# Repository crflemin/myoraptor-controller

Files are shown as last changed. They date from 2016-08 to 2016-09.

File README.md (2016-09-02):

# myoraptor-controller
This is the second iteration (but let's call it version 1.0) of a project combining the Raptor Reloaded 3D printed prosthetic with a MyoWare EMG sensor, a DC motor, and a Teensy 3.2. The goal is to build a prosthetic hand that responds to muscle contractions. I worked on the first iteration with an exceptional high school student who prototyped the design of the electronics control system using an Arduino Uno, breadboard, and wires. Shashi Jain designed the linear rail adapter and inspired us to combine the motor-driven Raptor with the MyoWare sensor. My contribution to this project was in pulling together the great work of these others and creating the PCB to slim down the device into something potentially wearable. I also want to thank <a href="https://github.com/wickerbox/">Wickerbox Electronics</a> for the KiCAD support and library resources!

This repository contains KiCAD design files for a PCB shield for the Teensy 3.2, as well as the Arduino code used to operate the hand.

Visit <a href="http://www.chloefleming.com/?p=90">my website</a> for pictures and more information.

## Components
1 x <a href="http://www.thingiverse.com/thing:596966">Raptor Reloaded</a> hand (scaled to 122%)</br>
1 x <a href="https://tinkercad.com/things/4MtmrpRE7Zj">linear rail adapter</a> for the Raptor Reloaded</br>
1 x <a href="https://www.adafruit.com/product/2699">MyoWare EMG sensor</a></br>
1 x <a href="https://oshpark.com/shared_projects/Pn4XONTR">MyoRaptor Controller PCB</a></br>
1 x DC motor (up to 12V)</br>

## Notes on Version 1.0
Here are some thoughts I have on the current working state of this project, and what should be done to improve future versions: </br>
* I am using a 9V battery to drive this circuit, but I am not convinced that this is moving the motor quickly enough and will likely look into other options.
* The DC motors with sufficient torque tend to be a bit bulky, and attaching them to the Raptor is not easy (this is currently being accomplished with a cheap plastic pipe clamp and a zip tie). A custom printed part should be designed to hold the motor. I'd also like to try to locate a smaller motor to power the hand.
* Right now, the PCB and linear rail adapter are sized to fit in the 122% hand. The linear rail should be made scalable with parameters and the PCB size may also need to be adjusted for smaller hands.
* The current version lacks a neat way to attach the PCB to the inside of the palm of the hand, which is another thing I'd like to improve with a printed part.

## Assembly Instructions
(in progress)

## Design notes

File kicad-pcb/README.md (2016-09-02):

# myoraptor-controller
A PCB shield for controlling the Raptor Reloaded 3D printed prosthetic with the MyoWare EMG sensor. KiCAD library references point to <a href="https://github.com/wickerbox/">Wickerbox Electronics</a>. 
Click <a href="https://oshpark.com/shared_projects/Pn4XONTR">here</a> to order this board from OSH Park!

## Board Previews
(Courtesy of OSH Park) </br>
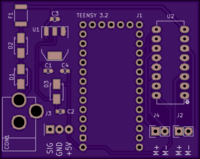
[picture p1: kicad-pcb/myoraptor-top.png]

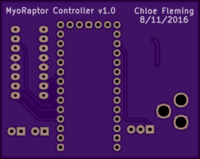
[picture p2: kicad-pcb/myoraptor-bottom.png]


## Bill of Materials
|Ref|Quantity|Digikey Part Number|Manufacturer Part Number|Description|
|---|--------|-------------------|------------------------|-----------|
|U2|1|296-9911-5-ND|SN754410NE|IC HALF-H DRVR QUAD 16-DIP|
|J2, J4|2|ED10561-ND|OSTVN02A150|CONN TERM BLOCK 2.54MM 2POS PCB|
|J3|1|OSTVN03A150|OSTVN03A150|CONN TERM BLOCK 2.54MM 3POS PCB|
|D1|1|SMAJ14A-FDICT-ND|SMAJ14A-13-F|TVS DIODE 14VWM 23.2VC SMA|
|U1|1|NCP1117LPST50T3GOSCT-ND|NCP1117LPST50T3G|IC REG LDO 5V 1A SOT223|
|F1|1|MF-MSMF110/24X-2CT-ND|MF-MSMF110/24X-2|FUSE PTC RESET 1.10A SMD 1812|
|D2, D3|2|SS12-E3/61TGICT-ND|SS12-E3/61T|DIODE SCHOTTKY 20V 1A DO214AC|
|C4|1|490-1519-1-ND|GRM188R71H104KA93D|CAP CER 0.1UF 50V X7R 0603|
|C3|1|490-5307-1-ND|GRM188R71E105KA12D|CAP CER 1UF 25V X7R 0603|
|C1, C2|2|490-7202-1-ND|GRM188R61E106MA73D|CAP CER 10UF 25V X5R 0603|
|J1|1|||Teensy 3.2|

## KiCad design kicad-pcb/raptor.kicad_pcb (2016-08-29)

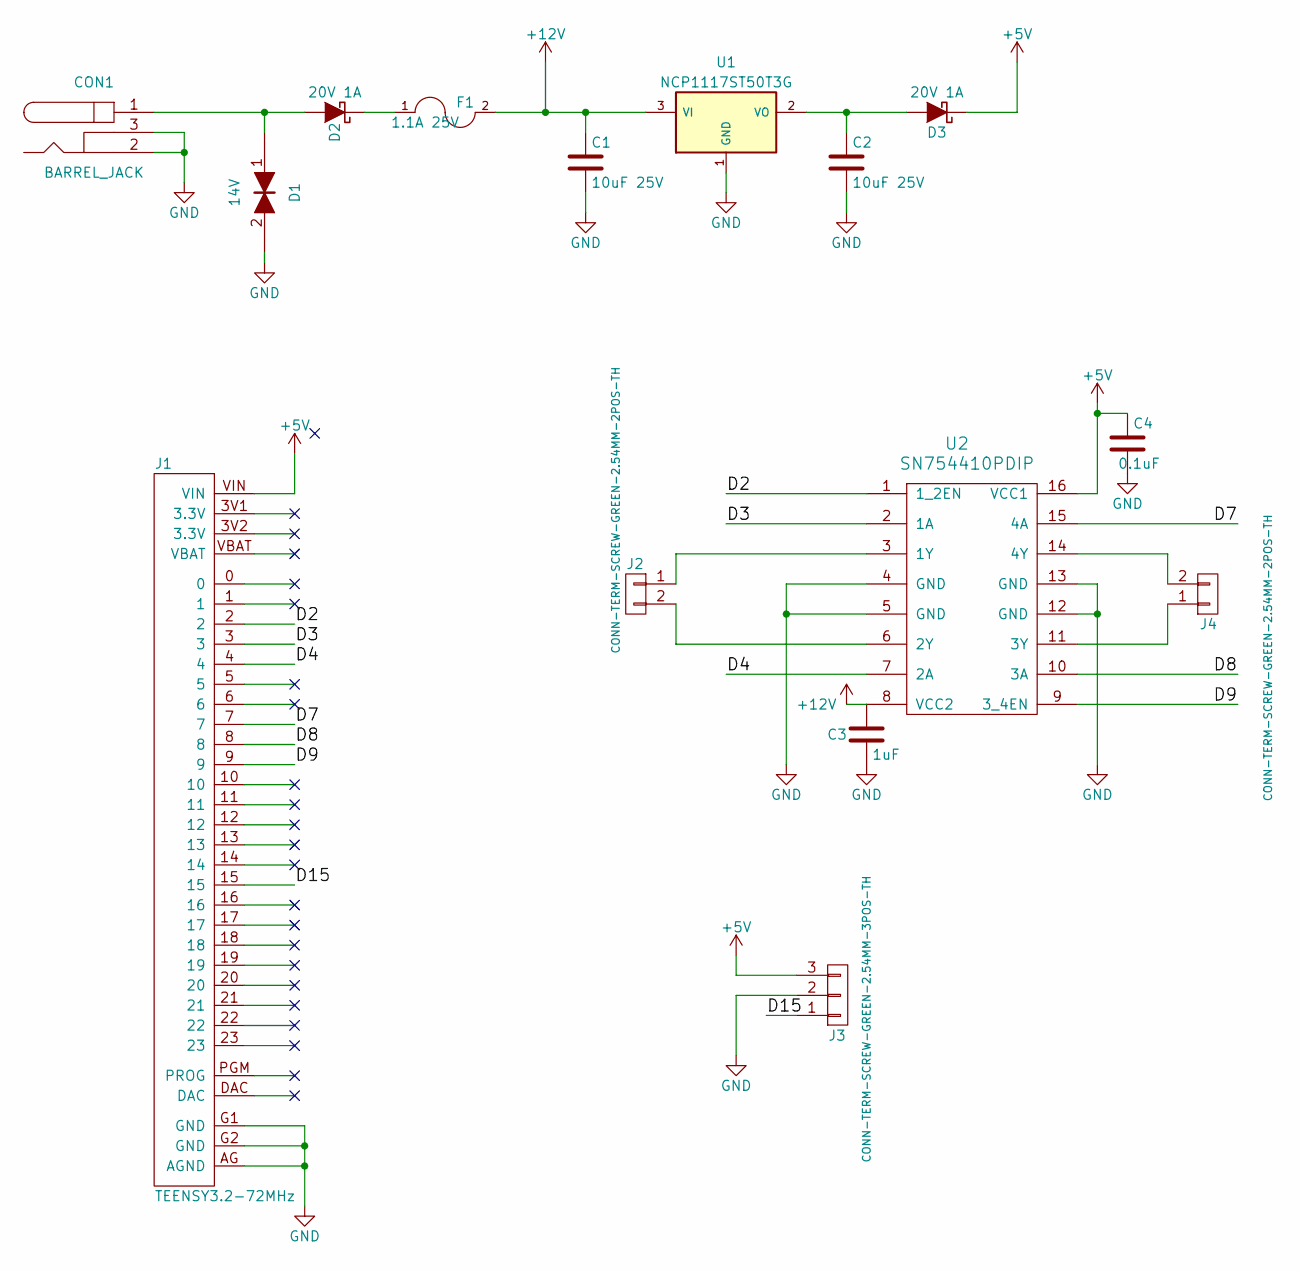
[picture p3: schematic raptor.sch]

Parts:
C1, C2: 10uF 25V; RLC-0603-SMD
C3: 1uF; RLC-0603-SMD
C4: 0.1uF; RLC-0603-SMD
CON1: BARREL_JACK; CONN-BARREL-JACK-2.5x5.5MM-TH
D1: 14V; DIODE-SMA
D2, D3: 20V 1A; DIODE-SMA
F1: 1.1A 25V; RLC-1812-SMD
J1: TEENSY3.2-72MHz; TEENSY-3.2-NOSILK
J2, J4: CONN-TERM-SCREW-GREEN-2.54MM-2POS-TH; CONN-ONSHORE-SCREW-GREEN-2PIN-TH
J3: CONN-TERM-SCREW-GREEN-2.54MM-3POS-TH; CONN-ONSHORE-SCREW-GREEN-3PIN-TH
U1: NCP1117ST50T3G; SOT-223
U2: SN754410PDIP; DIP-16-W7.62MM-LONGPADS

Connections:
+5V: C4.1, D3.1 (K), J1.VIN, J3.3, U2.16 (VCC1)
+12V: C1.1, C3.1, F1.2, U1.3 (VI), U2.8 (VCC2)
/D2: J1.2, U2.1 (1_2EN)
/D3: J1.3, U2.2 (1A)
/D4: J1.4, U2.7 (2A)
/D7: J1.7, U2.15 (4A)
/D8: J1.8, U2.10 (3A)
/D9: J1.9, U2.9 (3_4EN)
/D15: J1.15, J3.1
GND: C1.2, C2.2, C3.2, C4.2, CON1.2, CON1.3, D1.2, J1.AG (AGND), J1.G1 (GND), J1.G2 (GND), J3.2, U1.1 (GND), U2.4 (GND), U2.5 (GND), U2.12 (GND), U2.13 (GND)
unnamed: C2.1, D3.2 (A), U1.2 (VO)
unnamed: CON1.1, D1.1, D2.2 (A)
unnamed: D2.1 (K), F1.1
unnamed: J2.1, U2.3 (1Y)
unnamed: J2.2, U2.6 (2Y)
unnamed: J4.1, U2.11 (3Y)
unnamed: J4.2, U2.14 (4Y)

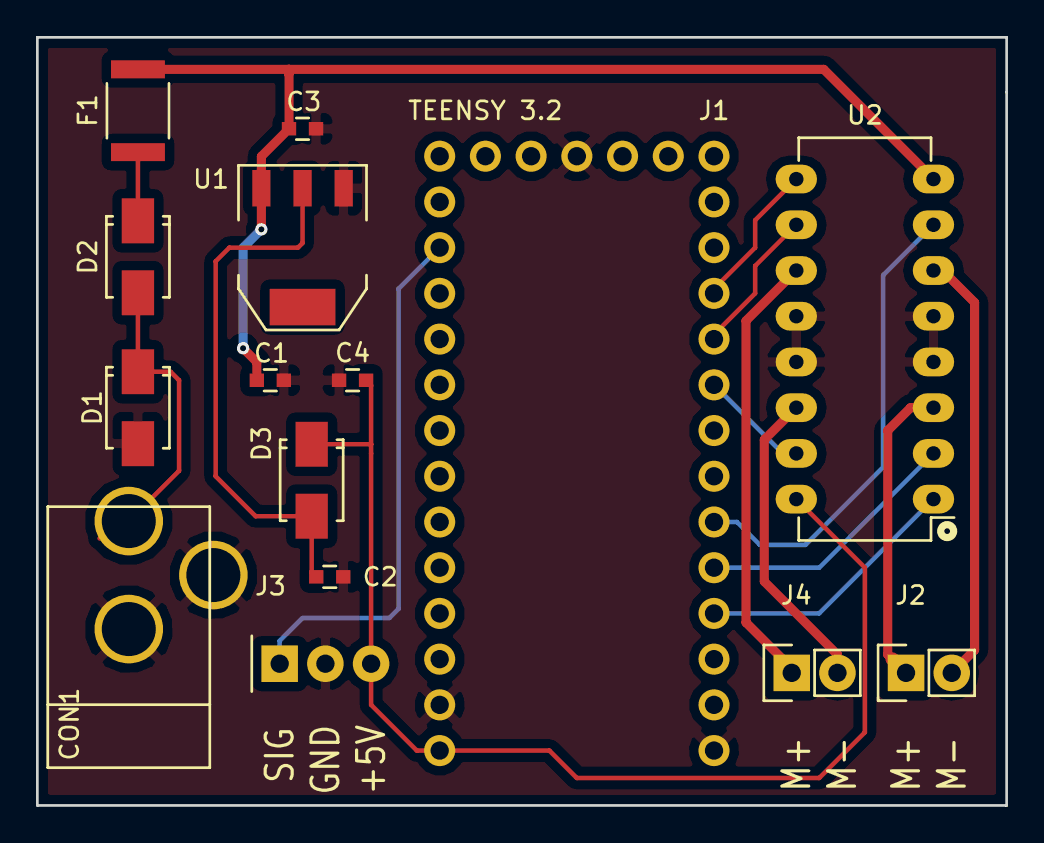
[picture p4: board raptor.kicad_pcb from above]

Board: 2 copper layers, 53.8 x 42.7 mm, 15 parts (0 on the bottom side), 17 nets.

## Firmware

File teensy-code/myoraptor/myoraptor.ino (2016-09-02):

#define ENABLE 2
#define MOTOR1 3
#define MOTOR2 4
#define LED    13
#define MYO    15

#define OPEN    1
#define CLOSED  0

int handState;

void setup() {
  // put your setup code here, to run once:
  pinMode(MYO, INPUT);
  pinMode(LED, OUTPUT);
  pinMode(MOTOR1, OUTPUT);
  pinMode(MOTOR2, OUTPUT);
  pinMode(ENABLE, OUTPUT);
  digitalWrite(ENABLE, HIGH);
  Serial.begin(9600);
  
  handState = OPEN;
}

void loop() {
  // put your main code here, to run repeatedly:
  int myoValue = analogRead(MYO);
  Serial.println(myoValue);
  
  if (handState == OPEN && myoValue > 400)
  {
    digitalWrite(MOTOR1, LOW);
    digitalWrite(MOTOR2, HIGH);
    digitalWrite(LED, HIGH);
    delay(2000);
    digitalWrite(MOTOR2, LOW);
    digitalWrite(MOTOR1, LOW);
    digitalWrite(LED, LOW);
    handState = CLOSED;
  }
  else if (handState == CLOSED && myoValue < 200)
  {
    digitalWrite(MOTOR1, HIGH);
    digitalWrite(MOTOR2, LOW);
    digitalWrite(LED, HIGH);
    delay(2000);
    digitalWrite(MOTOR2, LOW);
    digitalWrite(MOTOR1, LOW);
    digitalWrite(LED, LOW);
    handState = OPEN;
  }
}

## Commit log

2016-08-29 Initial commit of KiCAD files + gerbers
    [myoraptor-controller-BOM.csv, raptor-B.Cu.gbl, raptor-B.Fab.gbr, raptor-B.Mask.gbs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]
2016-08-29 Added bill of materials and board preview images
2016-08-29 Added organized subdirectories
    [myoraptor-controller-BOM.csv, raptor.kicad_pcb, raptor.sch]
2016-09-02 Adding first draft of controller code for Teensy
